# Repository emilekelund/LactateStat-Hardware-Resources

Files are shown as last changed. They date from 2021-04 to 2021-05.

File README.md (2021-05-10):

# LactateStat-Hardware-Resources

This is the hardware resources used in my master thesis: LactateStat: Wearable Electronics and Software for Real-Time Lactate Monitoring in Sweat

The PCB was created using KiCad version 5.1.6 and they were manufactured and assembled by PCBWay.

## Copyright disclaimer

Copyright (c) 2021 Emil Ekelund

Permission is hereby granted, free of charge, to any person obtaining a copy of this software and associated documentation files (the "Software"), to deal in the Software without restriction, including without limitation the rights to use, copy, modify, merge, publish, distribute, sublicense, and/or sell copies of the Software, and to permit persons to whom the Software is furnished to do so, subject to the following conditions:

The above copyright notice and this permission notice shall be included in all copies or substantial portions of the Software.

THE SOFTWARE IS PROVIDED "AS IS", WITHOUT WARRANTY OF ANY KIND, EXPRESS OR IMPLIED, INCLUDING BUT NOT LIMITED TO THE WARRANTIES OF MERCHANTABILITY, FITNESS FOR A PARTICULAR PURPOSE AND NONINFRINGEMENT. IN NO EVENT SHALL THE AUTHORS OR COPYRIGHT HOLDERS BE LIABLE FOR ANY CLAIM, DAMAGES OR OTHER LIABILITY, WHETHER IN AN ACTION OF CONTRACT, TORT OR OTHERWISE, ARISING FROM, OUT OF OR IN CONNECTION WITH THE SOFTWARE OR THE USE OR OTHER DEALINGS IN THE SOFTWARE.

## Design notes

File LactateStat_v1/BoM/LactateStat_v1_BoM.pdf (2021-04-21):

Item | Designator | Description / Value | Package | Manufacturer | Manufacturer part # | Quantity
1 | R205,R204 | 120 | R_0201_0603Metric | | | 2
2 | D201 | LED RED | D_0402_1005Metric | | | 1
3 | D202 | LED GREEN | D_0402_1005Metric | | | 1
4 | R202,R201 | 5.1k | R_0201_0603Metric | | | 2
5 | C101,C102,C112,C113 | 12pF NP0 2% | C_0402_1005Metric | | | 4
6 | C103,C104,C107,C301 | 100nF, X7R, 10% | C_0402_1005Metric | | | 4
7 | C105 | 4.7uF, X5R, 10% | C_0603_1608Metric | | | 1
8 | C106 | 1.0uF X7R 10% | C_0603_1608Metric | | | 1
9 | C108 | 100pF, NP0, 5% | C_0402_1005Metric | | | 1
10 | C110 | 0.8pF, NP0, 5% | C_0402_1005Metric | | | 1
11 | L101 | 3.9nH 5% | L_0402_1005Metric | | | 1
12 | U101 | NRF52832-QFAB-R | 48-VFQFN | | | 1
13 | X101 | 32.768kHz 9pF 20ppm | Crystal_SMD_3215-2Pin_3.2x1.5mm | | | 1
14 | X102 | 32MHz 8pF 10ppm | Crystal_SMD_2016-4Pin_2.0x1.6mm | | | 1
15 | C201,C202 | 4.7uF X7R | C_0402_1005Metric | | | 2
16 | C203,C204 | 1uF | C_0402_1005Metric | | | 2
17 | C302 | 2.2uF | C_0201_0603Metric | | | 1
18 | C303 | 82nF 10% | C_0402_1005Metric | | | 1
20 | J201 | USB C RECEPTACLE | GCT_USB4105_REVA | GCT | USB4110-GF-A | 1
23 | R203 | 10k | R_0402_1005Metric | | | 1
24 | R301 | 10k | R_0201_0603Metric | | | 1
25 | R302 | 1.5M 1% | R_0402_1005Metric | | | 1
26 | SW201 | SW_SPDT | CL-SB-12B | Nidec Copal Electronics | CL-SB-12B-01T | 1
27 | U201 | MCP73831 | SOT-23-5 | | | 1
28 | U202 | TLV73333PDBV | SOT-23-5 | | | 1
29 | U301 | LMP91000SD_NOPB | WSON-14-1EP_4.0x4.0mm_P0.5mm_EP2.6x2.6mm | | | 1

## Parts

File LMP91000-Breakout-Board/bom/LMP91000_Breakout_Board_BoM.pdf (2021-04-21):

Id Designator Package | Quantity Designation | Supplier and ref | Unit Price ($)
1 LMP91000 WSON-14-1EP_4.0x4.0mm_P0.5mm_EP2.6x2.6mm | 1 LMP91000SD_NOPB Texas Instruments LMP91000SD/NOPB | 5
2 R2,R1 | R_0603_1608Metric_Pad1.05x0.95mm_HandSolder | 2 10K | Stackpole Electronics Inc RNCP0603FTD10K0 | 0,1
3 C2 | C_0603_1608Metric_Pad1.05x0.95mm_HandSolder | 1 1u | Samsung Electro-Mechanics CL10B104KB8NNNL | 0,1
4 C1 | C_0603_1608Metric_Pad1.05x0.95mm_HandSolder | 1 0.1u | Samsung Electro-Mechanics CL10B105KP8NNNC | 0,1

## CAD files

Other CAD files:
Case/LactateStat_3D_Printed_Case.dwg

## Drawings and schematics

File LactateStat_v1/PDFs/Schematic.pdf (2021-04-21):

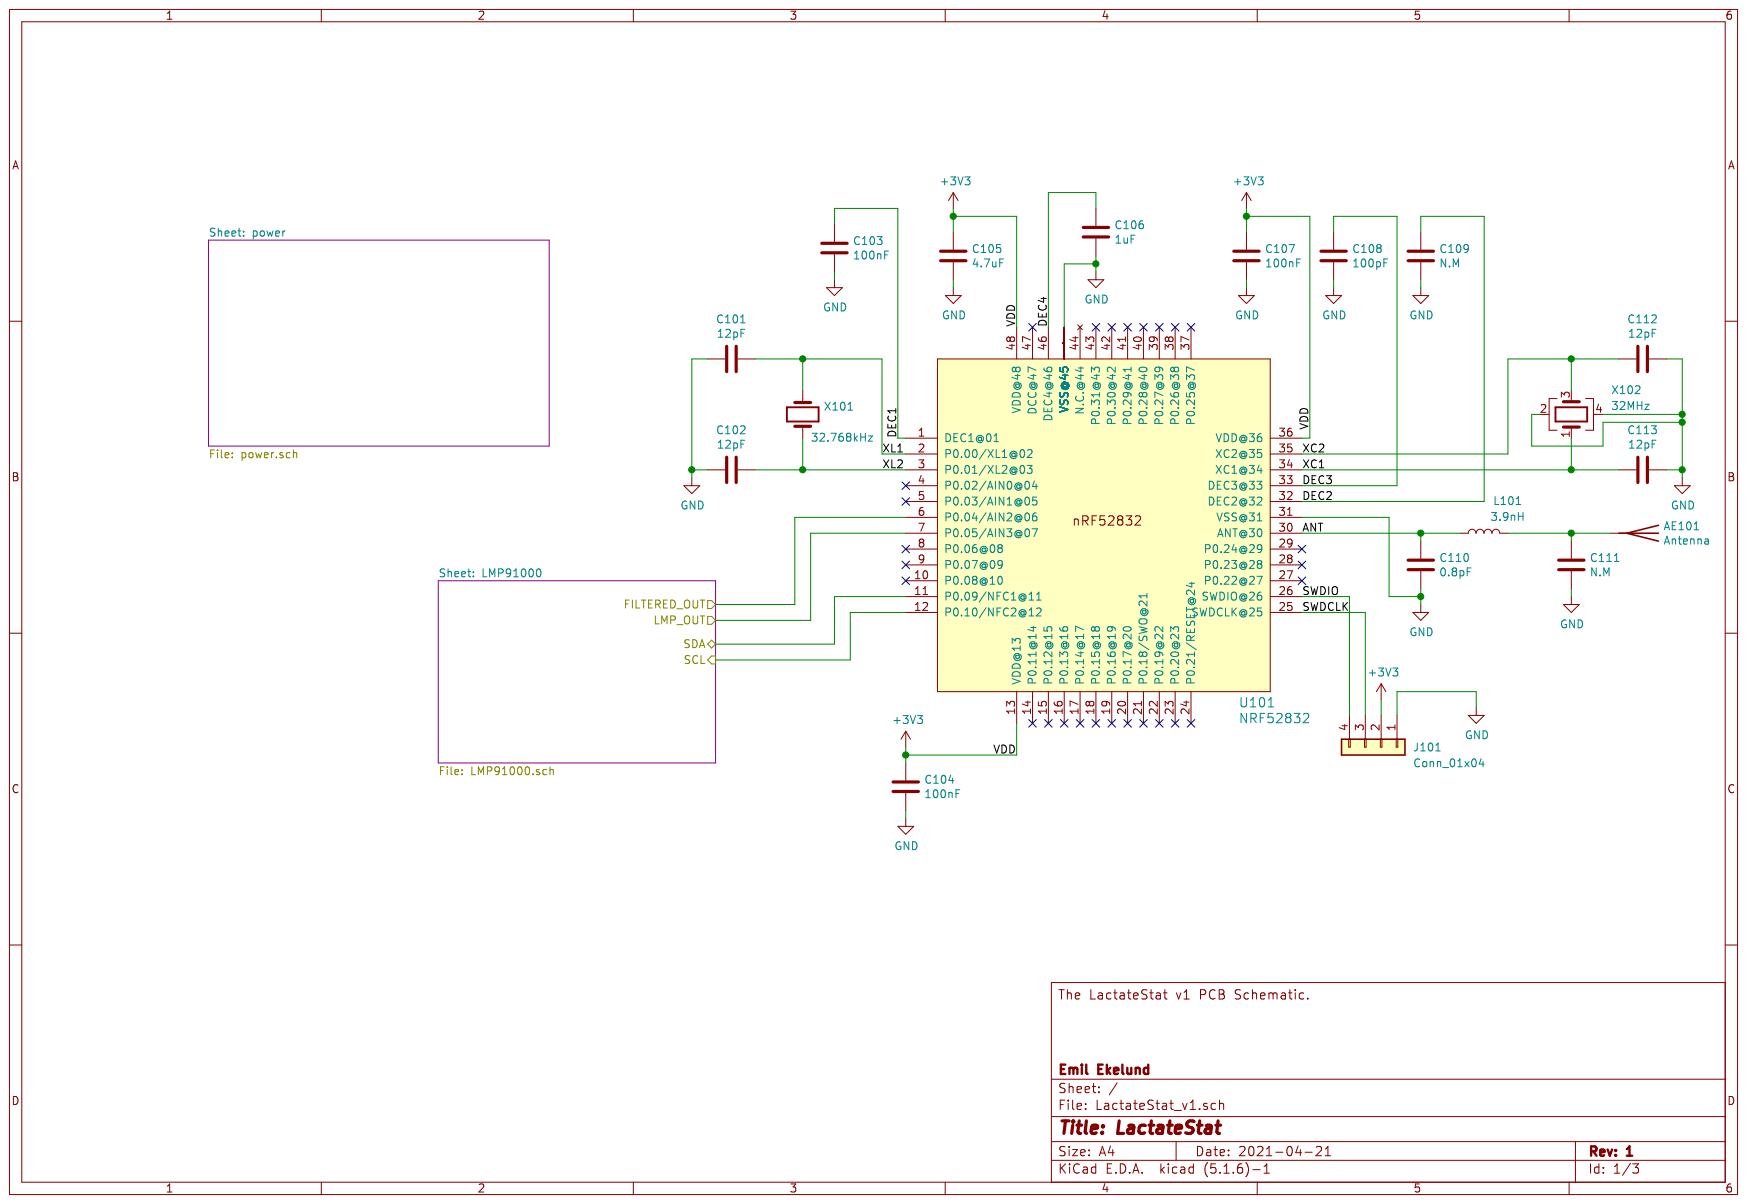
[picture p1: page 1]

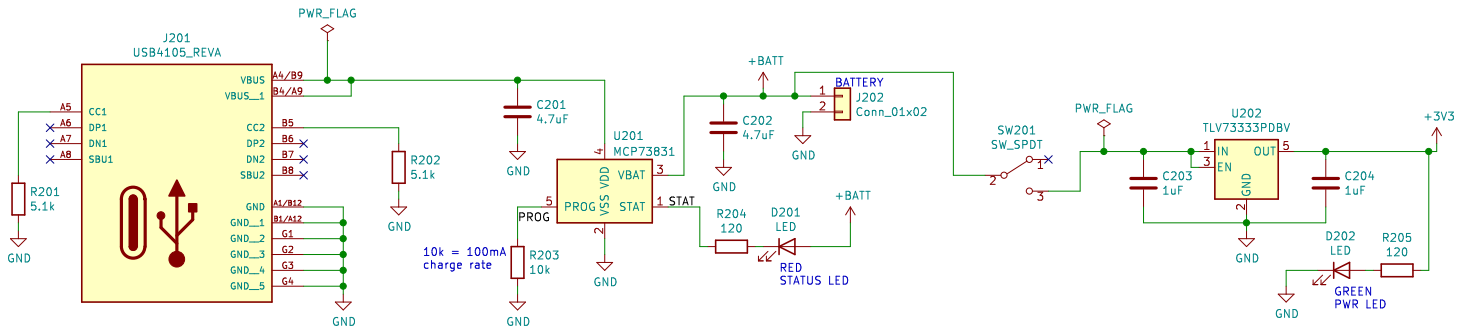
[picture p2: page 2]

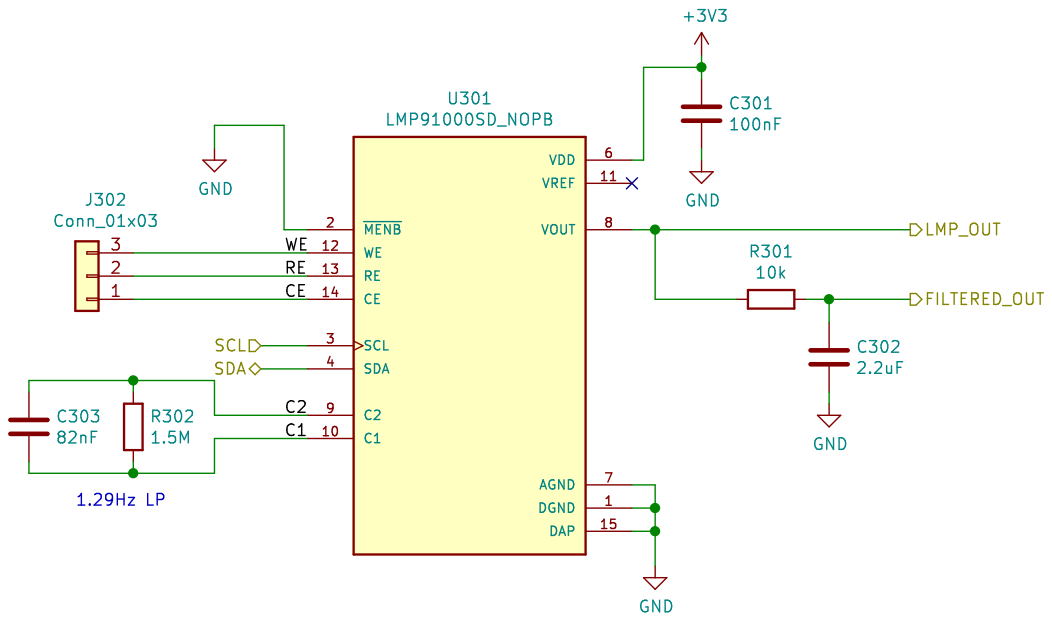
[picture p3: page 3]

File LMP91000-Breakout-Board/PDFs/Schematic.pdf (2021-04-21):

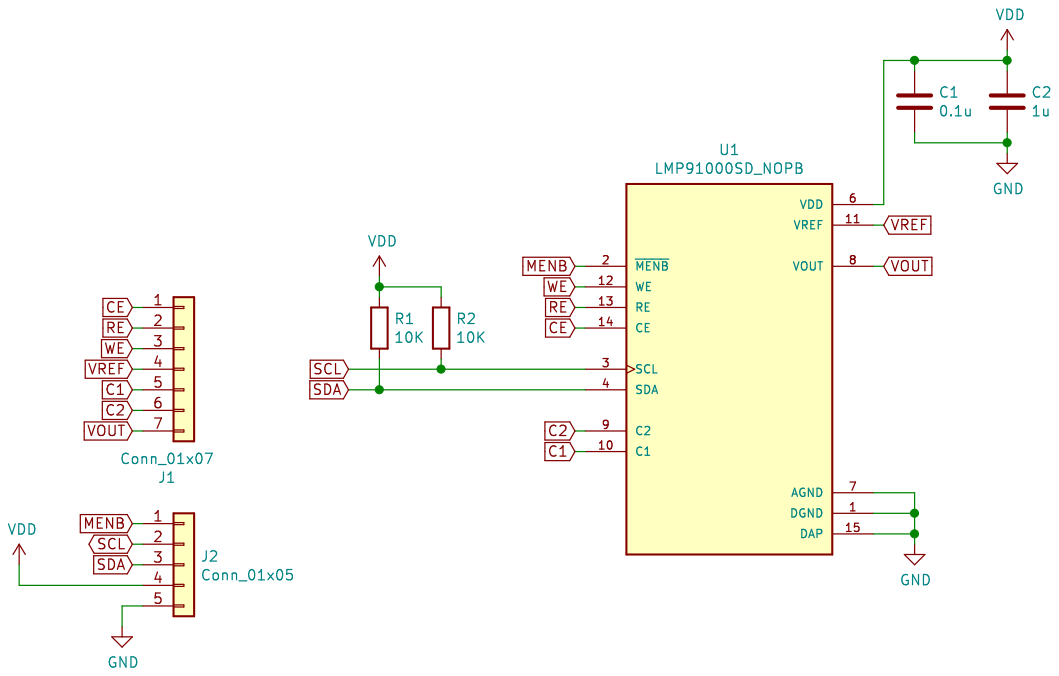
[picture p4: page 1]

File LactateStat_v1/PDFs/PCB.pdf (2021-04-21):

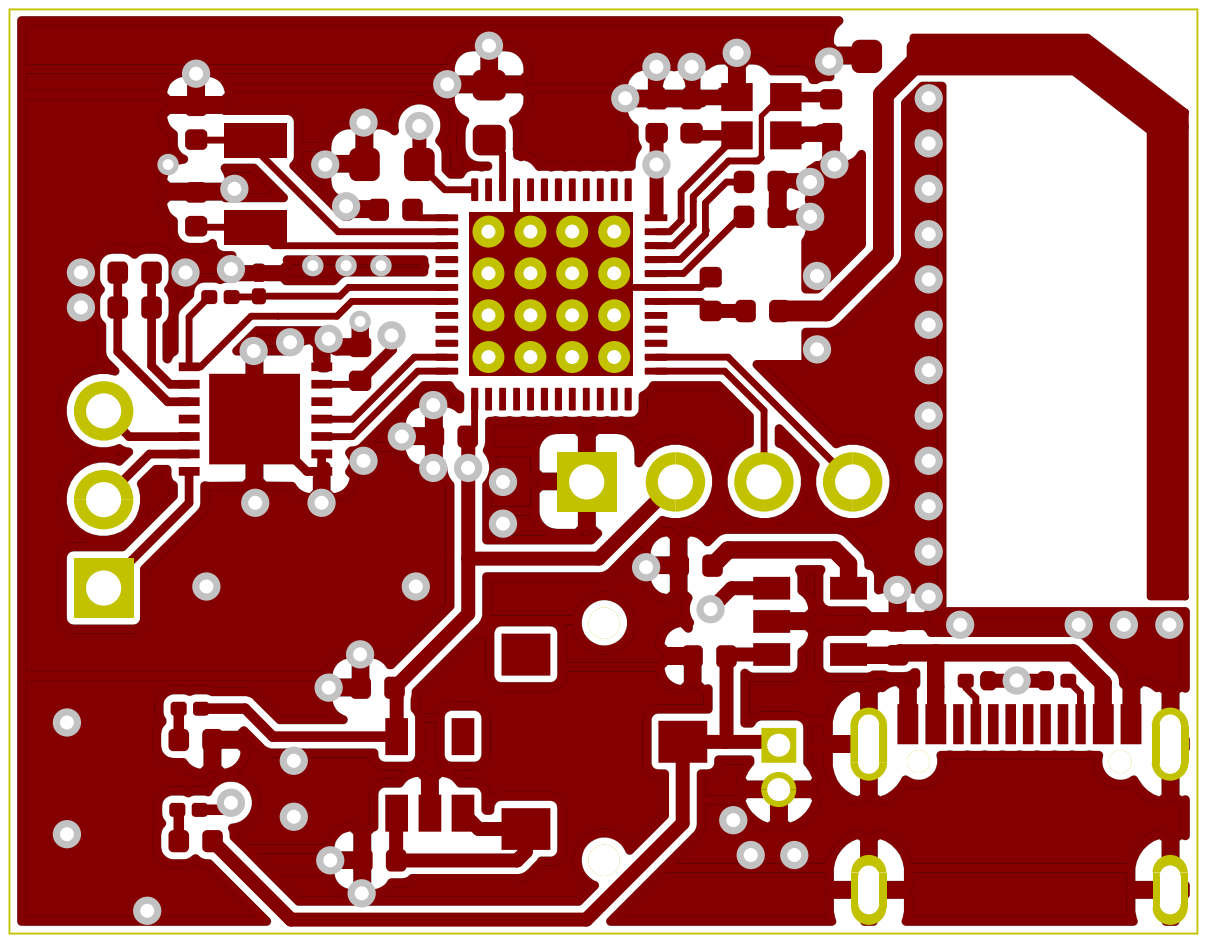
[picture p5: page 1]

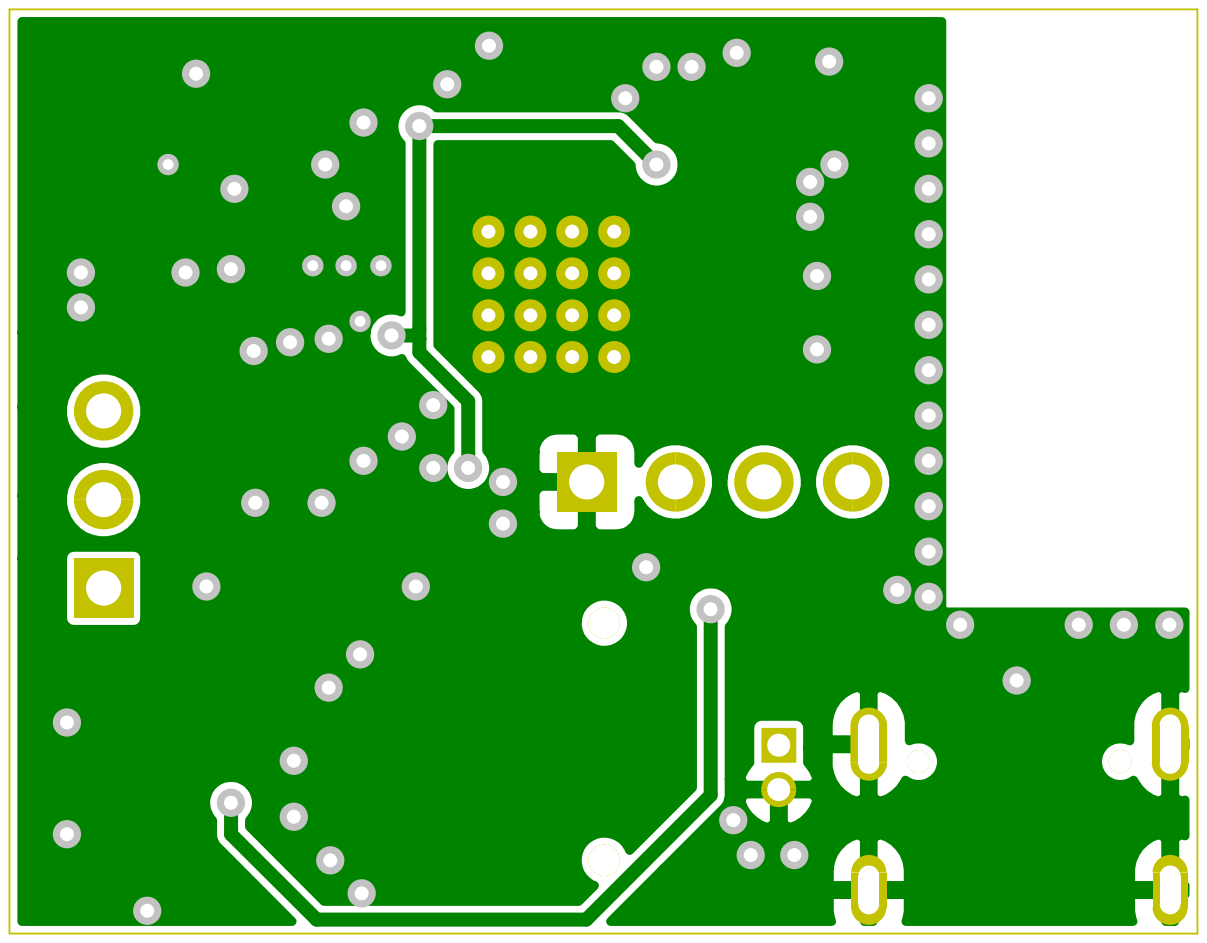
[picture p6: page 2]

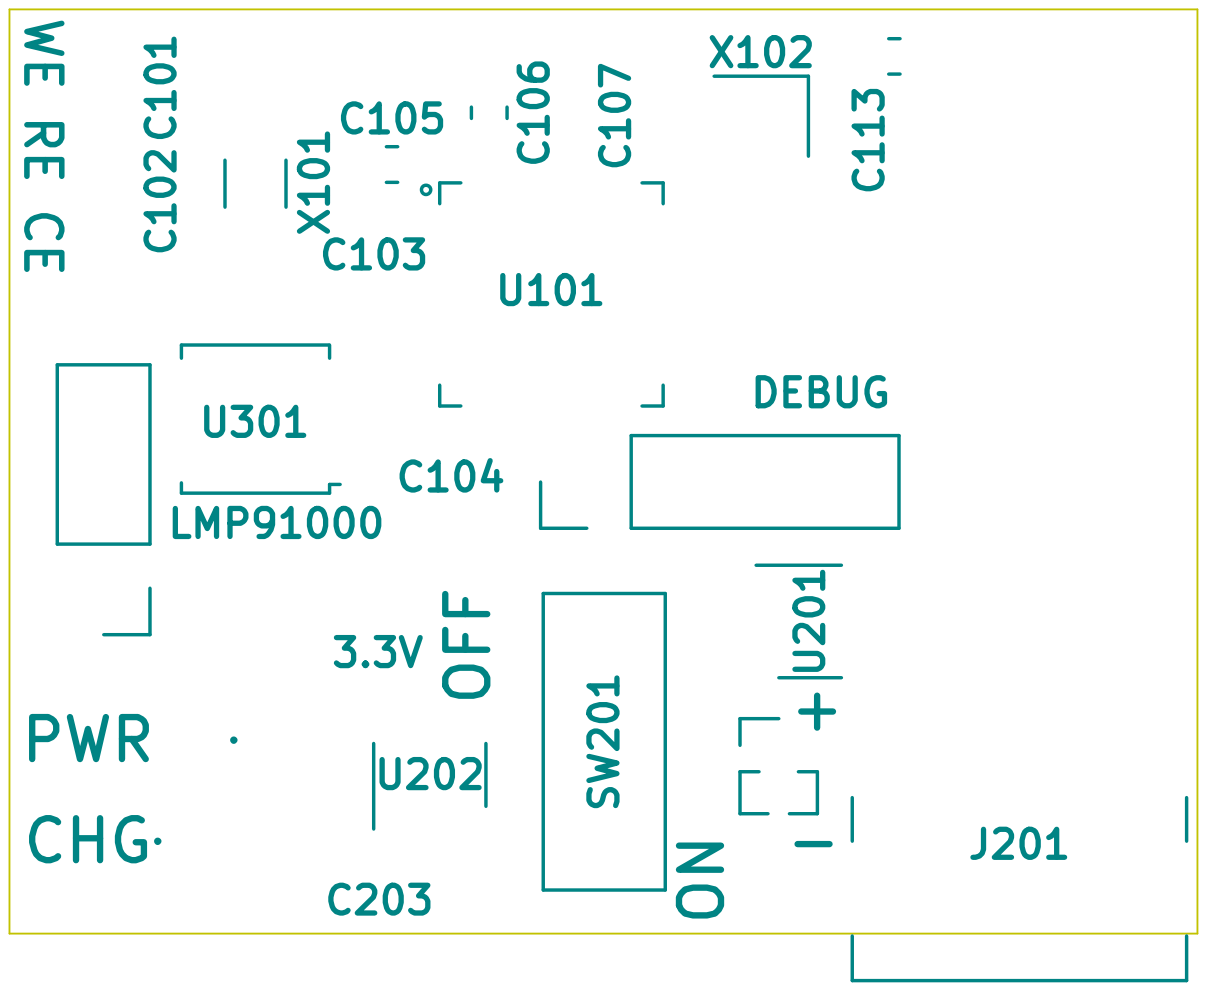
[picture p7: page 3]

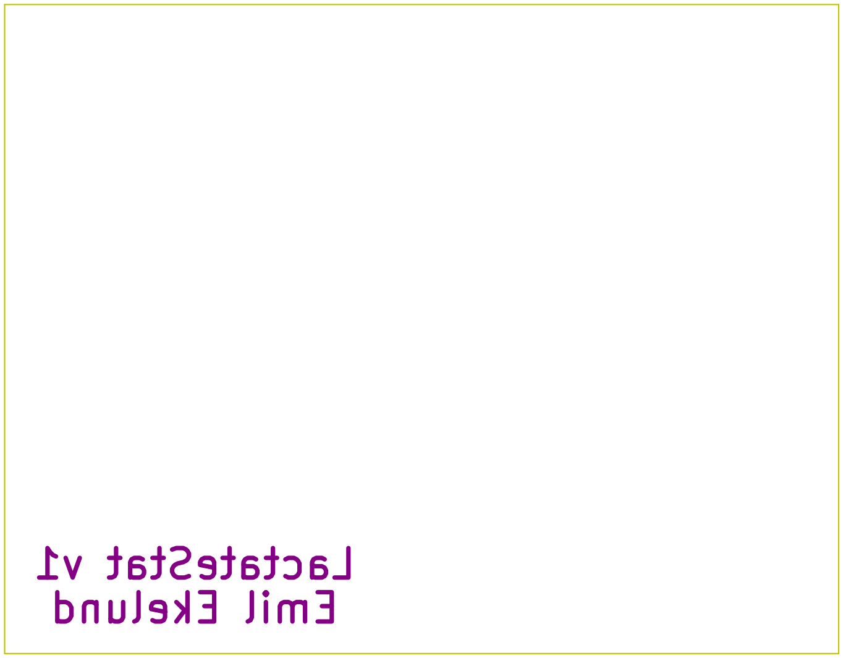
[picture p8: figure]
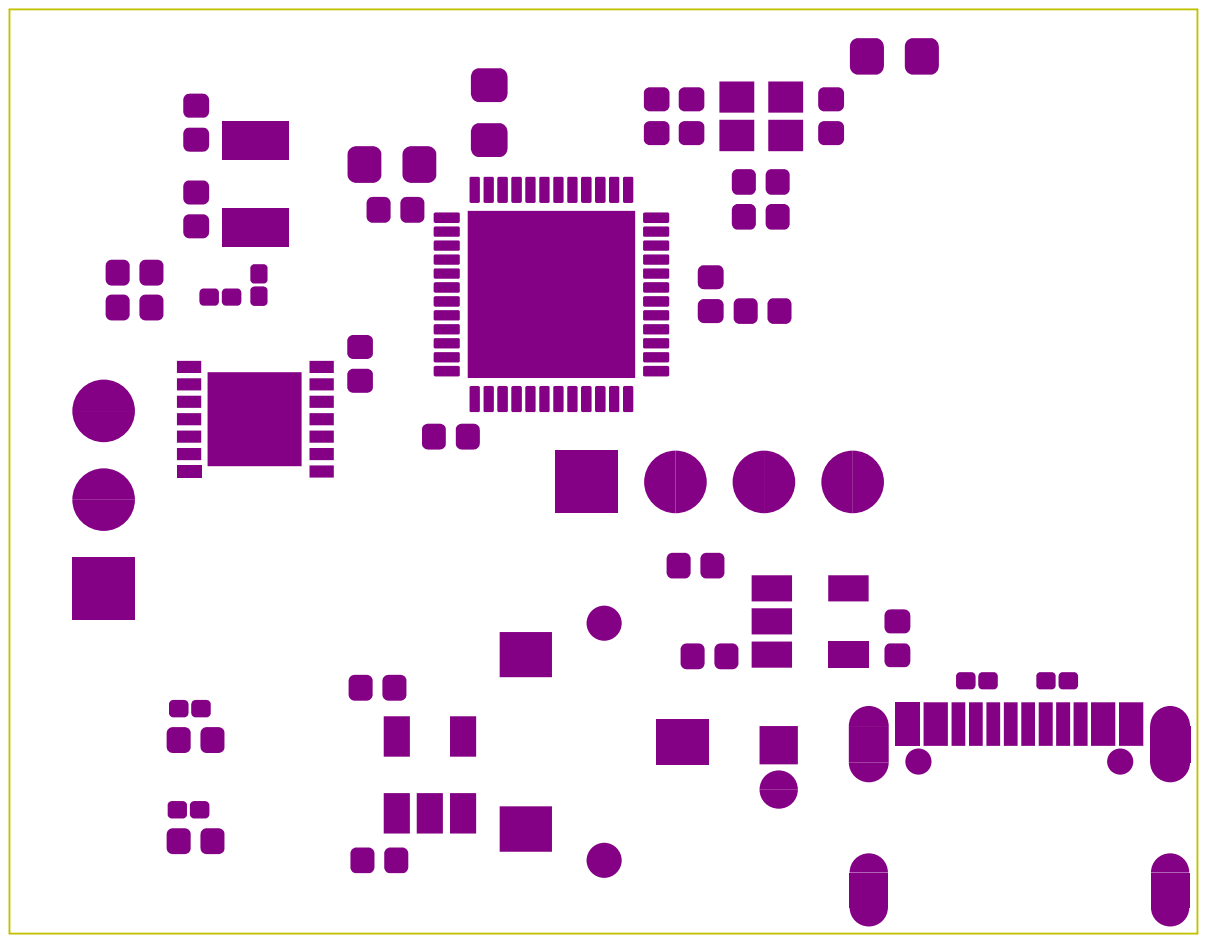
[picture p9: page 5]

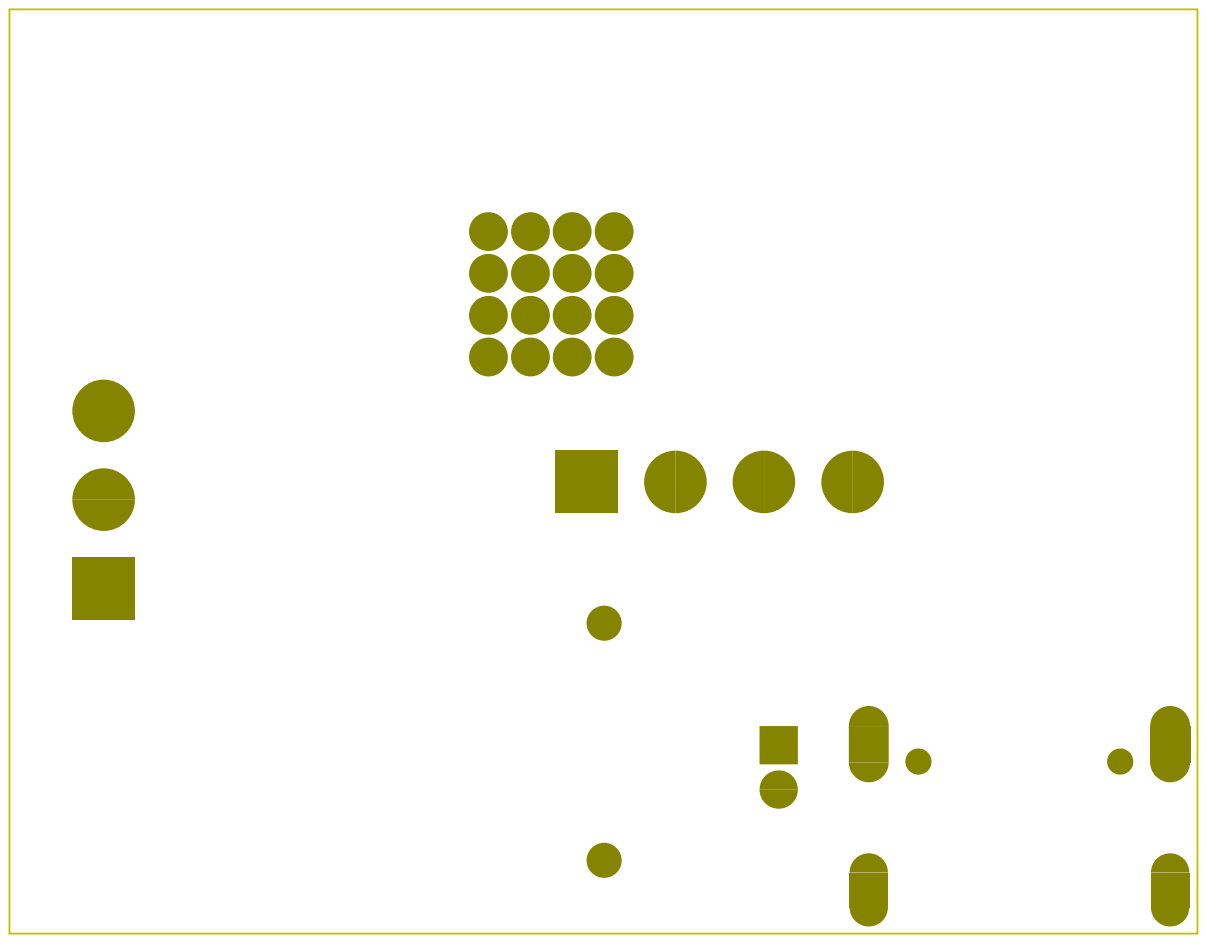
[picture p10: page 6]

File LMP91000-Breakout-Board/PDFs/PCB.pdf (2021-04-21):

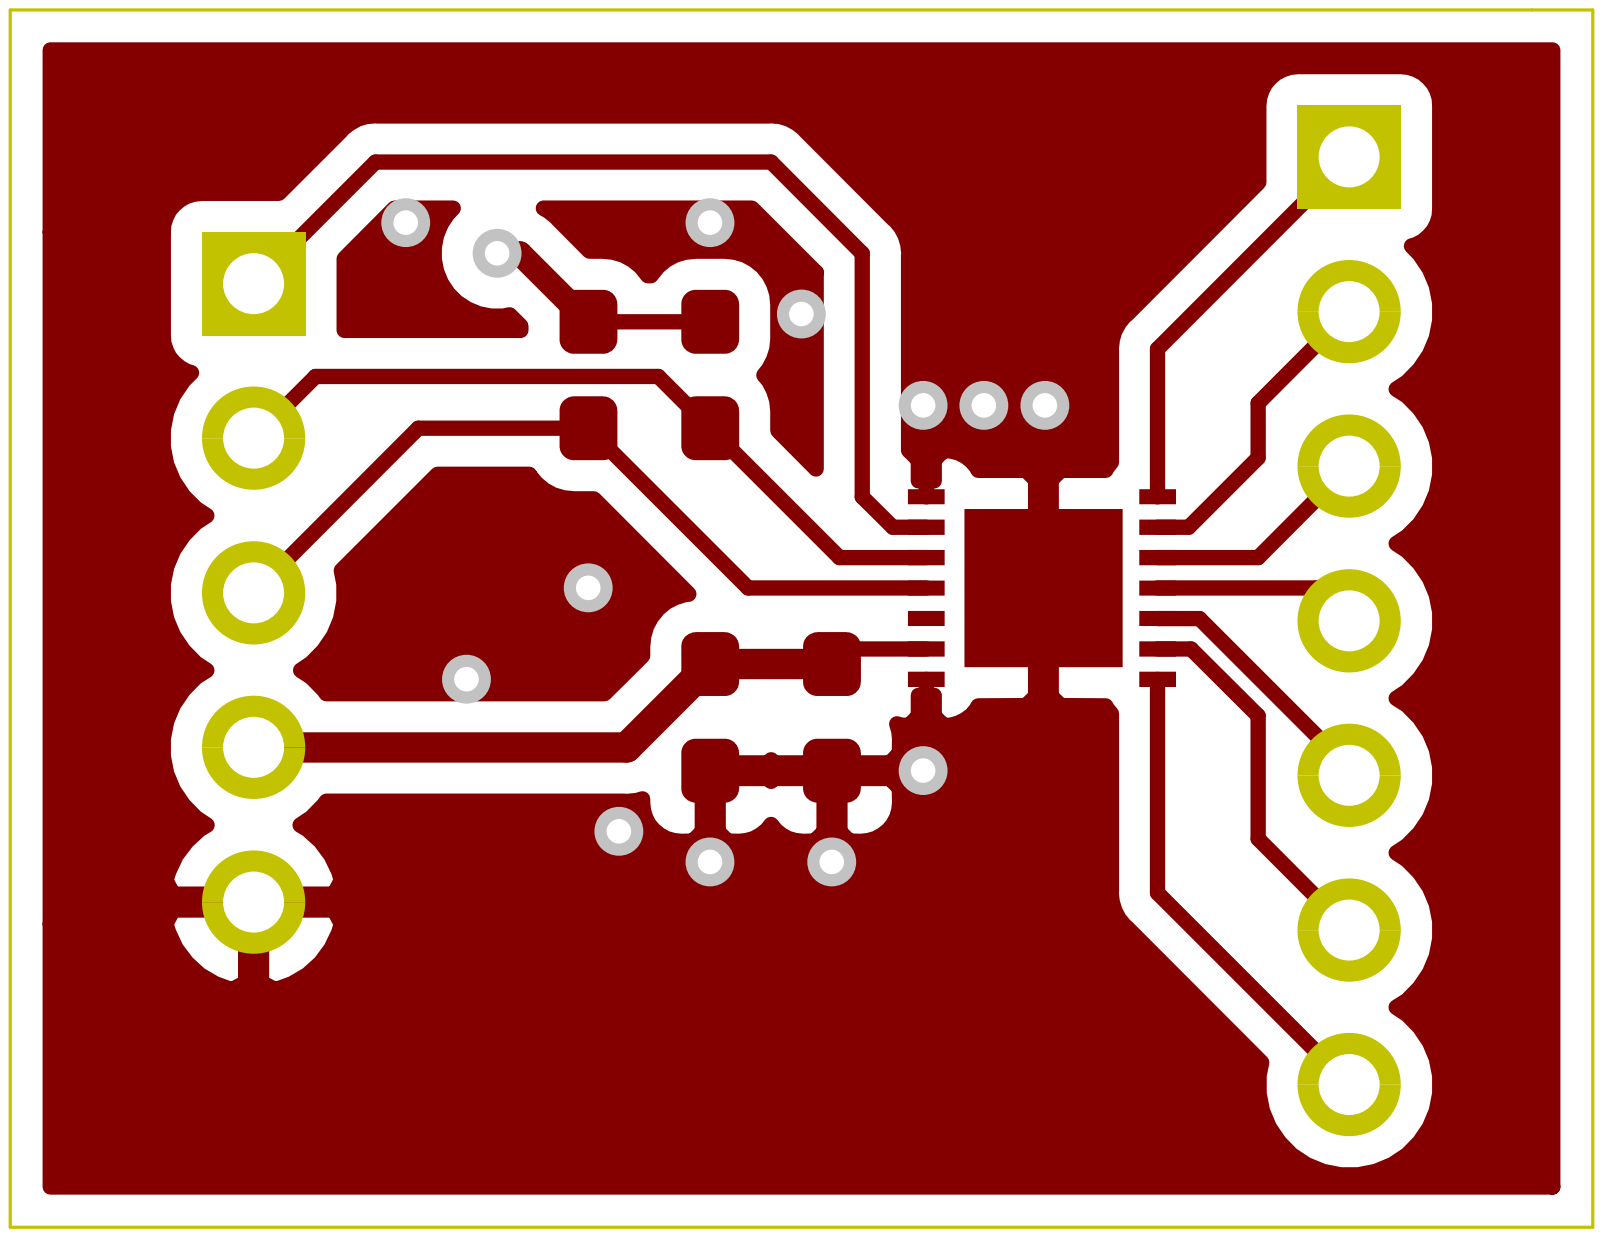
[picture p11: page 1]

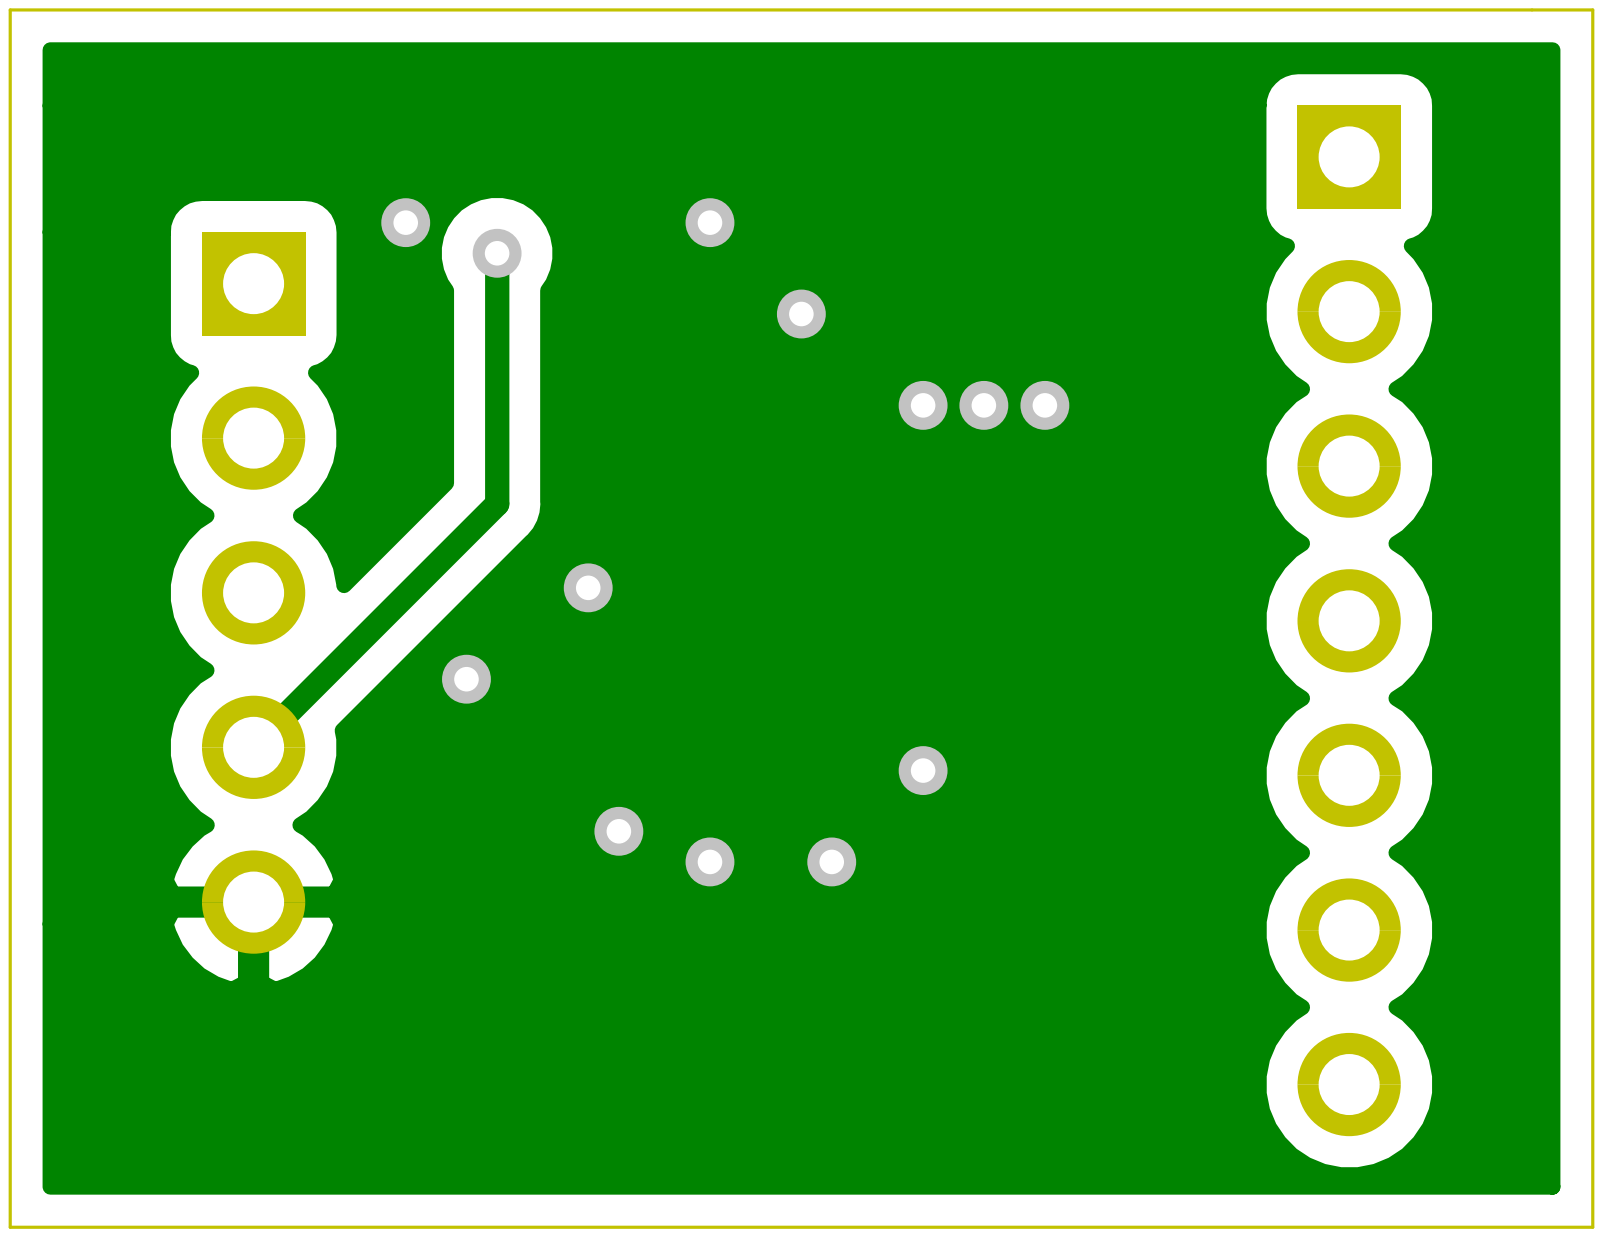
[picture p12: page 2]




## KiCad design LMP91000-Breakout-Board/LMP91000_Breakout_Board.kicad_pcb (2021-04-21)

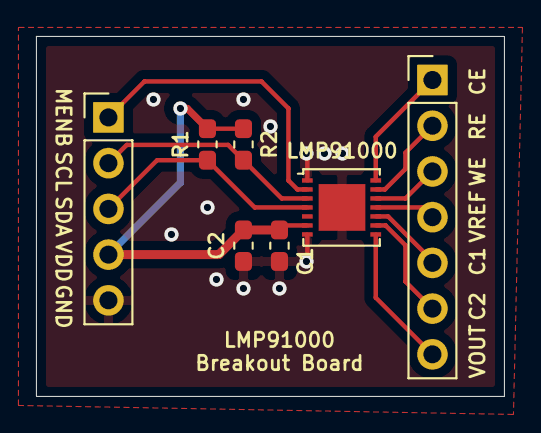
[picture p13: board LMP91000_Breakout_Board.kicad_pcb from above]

Board: 2 copper layers, 26.0 x 20.0 mm, 7 parts (0 on the bottom side), 12 nets.

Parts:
C1: 0.1u; C_0603_1608Metric_Pad1.05x0.95mm_HandSolder
C2: 1u; C_0603_1608Metric_Pad1.05x0.95mm_HandSolder
J1: Conn_01x07; PinHeader_1x07_P2.54mm_Vertical
J2: Conn_01x05; PinHeader_1x05_P2.54mm_Vertical
LMP91000: LMP91000SD_NOPB; WSON-14-1EP_4.0x4.0mm_P0.5mm_EP2.6x2.6mm
R1, R2: 10K; R_0603_1608Metric_Pad1.05x0.95mm_HandSolder

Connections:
C1: J1.5, LMP91000.10
C2: J1.6, LMP91000.9
CE: J1.1, LMP91000.14
GND: C1.2, C2.2, J2.5, LMP91000.1, LMP91000.7, LMP91000.15
MENB: J2.1, LMP91000.2
RE: J1.2, LMP91000.13
SCL: J2.2, LMP91000.3, R2.2
SDA: J2.3, LMP91000.4, R1.2
VDD: C1.1, C2.1, J2.4, LMP91000.6, R1.1, R2.1
VOUT: J1.7, LMP91000.8
VREF: J1.4, LMP91000.11
WE: J1.3, LMP91000.12

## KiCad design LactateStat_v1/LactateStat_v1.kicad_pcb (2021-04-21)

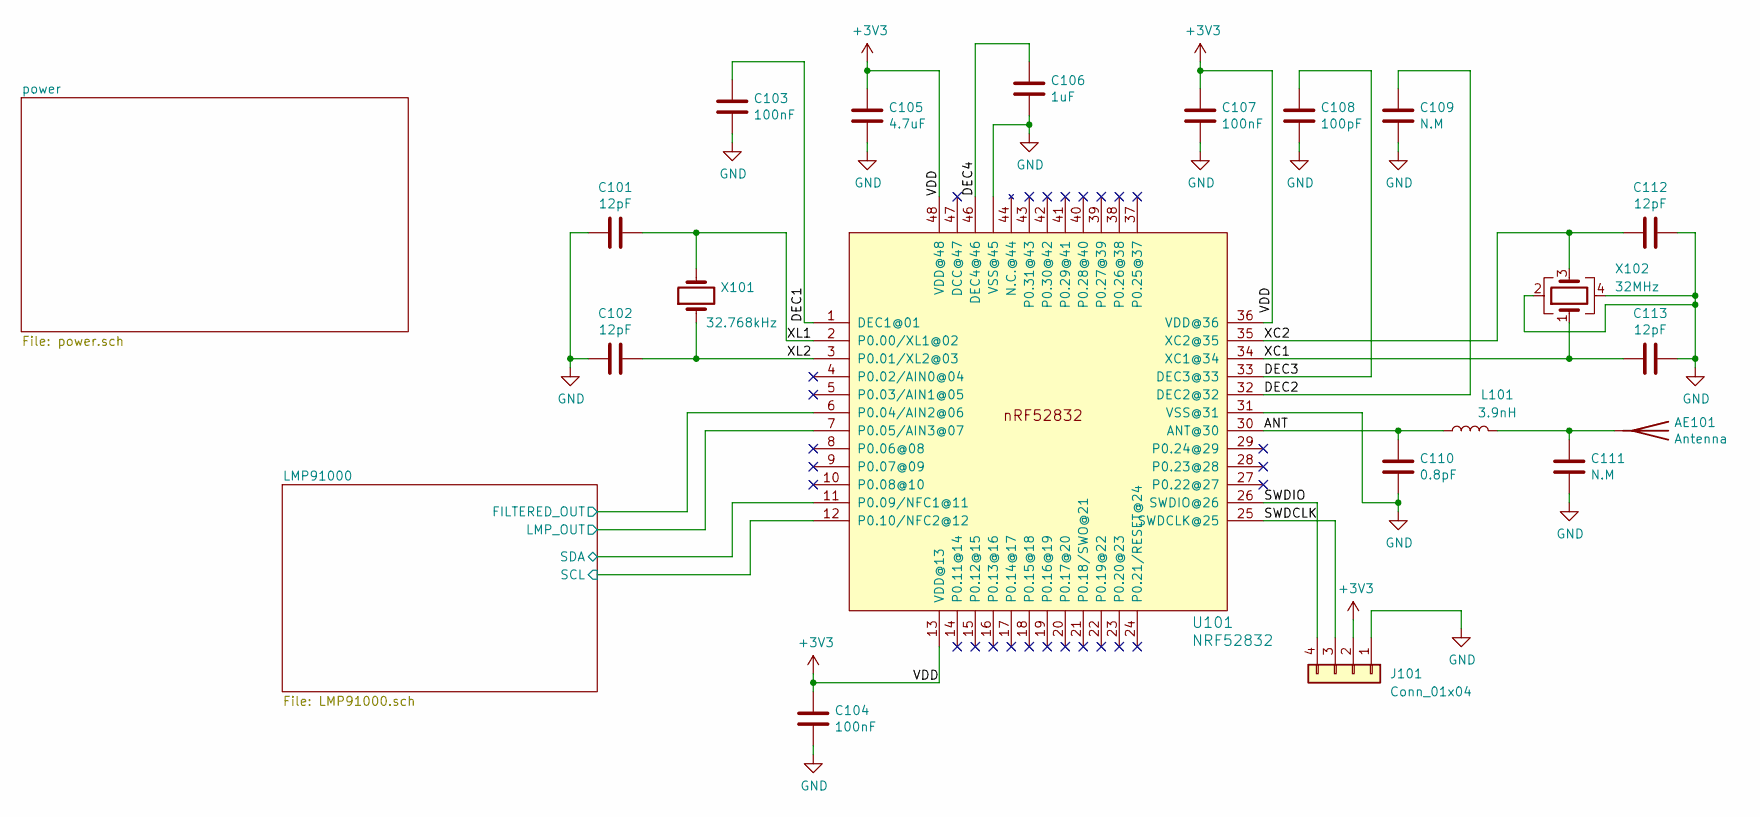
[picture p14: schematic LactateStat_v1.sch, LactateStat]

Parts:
AE101: Antenna
C101, C102, C112, C113: 12pF; C_0402_1005Metric
C103, C104, C107: 100nF; C_0402_1005Metric
C105: 4.7uF; C_0603_1608Metric
C106: 1uF; C_0603_1608Metric
C108: 100pF; C_0402_1005Metric
C109: N.M; C_0402_1005Metric
C110: 0.8pF; C_0402_1005Metric
C111: N.M; C_0603_1608Metric
J101: Conn_01x04; PinHeader_1x04_P2.54mm_Vertical
L101: 3.9nH; L_0402_1005Metric
U101: NRF52832; nRF52832_with_via_pads
X101: 32.768kHz; Crystal_SMD_3215-2Pin_3.2x1.5mm
X102: 32MHz; Crystal_SMD_2016-4Pin_2.0x1.6mm

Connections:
+3V3: C104.1, C105.1, C107.1, J101.2, U101.13 (VDD@13), U101.36 (VDD@36), U101.48 (VDD@48); also elsewhere on the board
/ANT: C110.1, L101.1, U101.30 (ANT@30)
/DEC1: C103.1, U101.1 (DEC1@01)
/DEC2: C109.1, U101.32 (DEC2@32)
/DEC3: C108.1, U101.33 (DEC3@33)
/DEC4: C106.1, U101.46 (DEC4@46)
/LMP91000/FILTERED_OUT: U101.6 (P0.04/AIN2@06); also elsewhere on the board
/LMP91000/LMP_OUT: U101.7 (P0.05/AIN3@07); also elsewhere on the board
/LMP91000/SCL: U101.12 (P0.10/NFC2@12); also elsewhere on the board
/LMP91000/SDA: U101.11 (P0.09/NFC1@11); also elsewhere on the board
/SWDCLK: J101.3, U101.25 (SWDCLK@25)
/SWDIO: J101.4, U101.26 (SWDIO@26)
/XC1: C113.2, U101.34 (XC1@34), X102.1
/XC2: C112.2, U101.35 (XC2@35), X102.3
/XL1: C101.1, U101.2 (P0.00/XL1@02), X101.2
/XL2: C102.1, U101.3 (P0.01/XL2@03), X101.1
GND: C101.2, C102.2, C103.2, C104.2, C105.2, C106.2, C107.2, C108.2, C109.2, C110.2, C111.2, C112.1, C113.1, J101.1, U101.31 (VSS@31), U101.45 (VSS@45), U101.PAD (VSS@45), U101.PAD@VIA01 (VSS@45), U101.PAD@VIA02 (VSS@45), U101.PAD@VIA03 (VSS@45), U101.PAD@VIA04 (VSS@45), U101.PAD@VIA05 (VSS@45), U101.PAD@VIA06 (VSS@45), U101.PAD@VIA07 (VSS@45), U101.PAD@VIA08 (VSS@45), U101.PAD@VIA09 (VSS@45), U101.PAD@VIA10 (VSS@45), U101.PAD@VIA11 (VSS@45), U101.PAD@VIA12 (VSS@45), U101.PAD@VIA13 (VSS@45), U101.PAD@VIA14 (VSS@45), U101.PAD@VIA15 (VSS@45), U101.PAD@VIA16 (VSS@45), X102.2, X102.4; also elsewhere on the board
unnamed: AE101.1, C111.1, L101.2

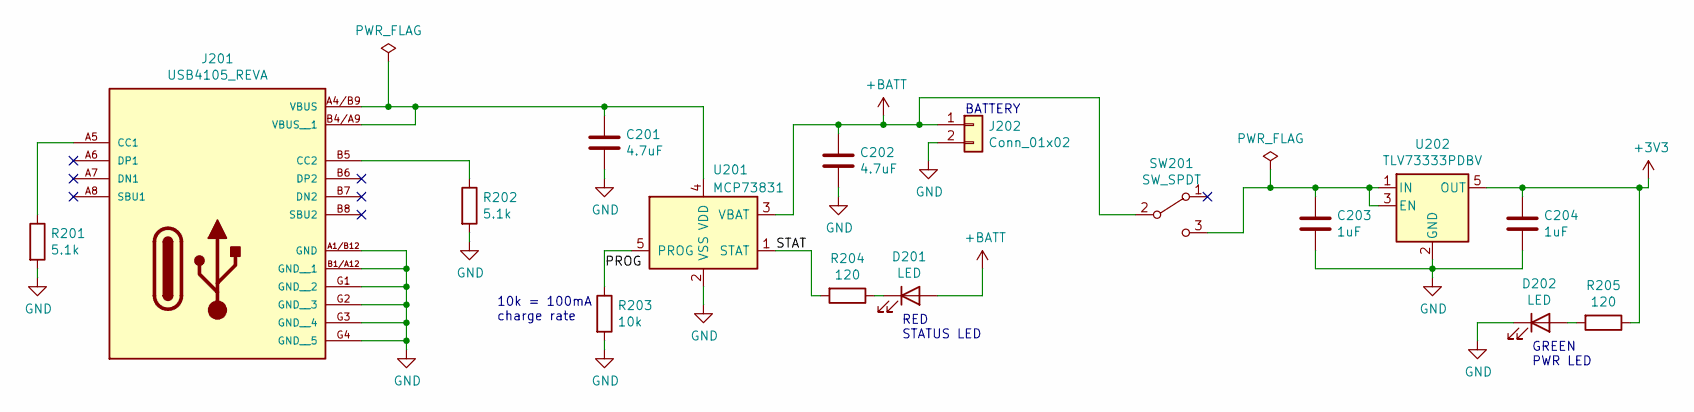
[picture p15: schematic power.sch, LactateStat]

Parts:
C201, C202: 4.7uF; C_0402_1005Metric
C203, C204: 1uF; C_0402_1005Metric
D201, D202: LED; D_0402_1005Metric
J201: USB4105_REVA; GCT_USB4105_REVA
J202: Conn_01x02; PinHeader_1x02_P1.27mm_Vertical
R201, R202: 5.1k; R_0201_0603Metric
R203: 10k; R_0402_1005Metric
R204, R205: 120; R_0201_0603Metric
SW201: SW_SPDT; CL-SB-12B
U201: MCP73831; SOT-23-5
U202: TLV73333PDBV; SOT-23-5

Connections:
+3V3: C204.1, R205.1, U202.5 (OUT); also elsewhere on the board
+BATT: C202.1, D201.2 (A), J202.1, SW201.2 (B), U201.3 (VBAT)
/power/PROG: R203.1, U201.5 (PROG)
/power/STAT: R204.2, U201.1 (STAT)
GND: C201.2, C202.2, C203.2, C204.2, D202.1 (K), J201.A1/B12 (GND), J201.B1/A12 (GND__1), J201.G1 (GND__2), J201.G2 (GND__3), J201.G3 (GND__4), J201.G4 (GND__5), J202.2, R201.2, R202.2, R203.2, U201.2 (VSS), U202.2 (GND); also elsewhere on the board
unnamed: C201.1, J201.A4/B9 (VBUS), J201.B4/A9 (VBUS__1), U201.4 (VDD)
unnamed: C203.1, SW201.3 (C), U202.1 (IN), U202.3 (EN)
unnamed: D201.1 (K), R204.1
unnamed: D202.2 (A), R205.2
unnamed: J201.A5 (CC1), R201.1
unnamed: J201.B5 (CC2), R202.1

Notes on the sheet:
10k = 100mA charge rate
RED STATUS LED
GREEN PWR LED
BATTERY

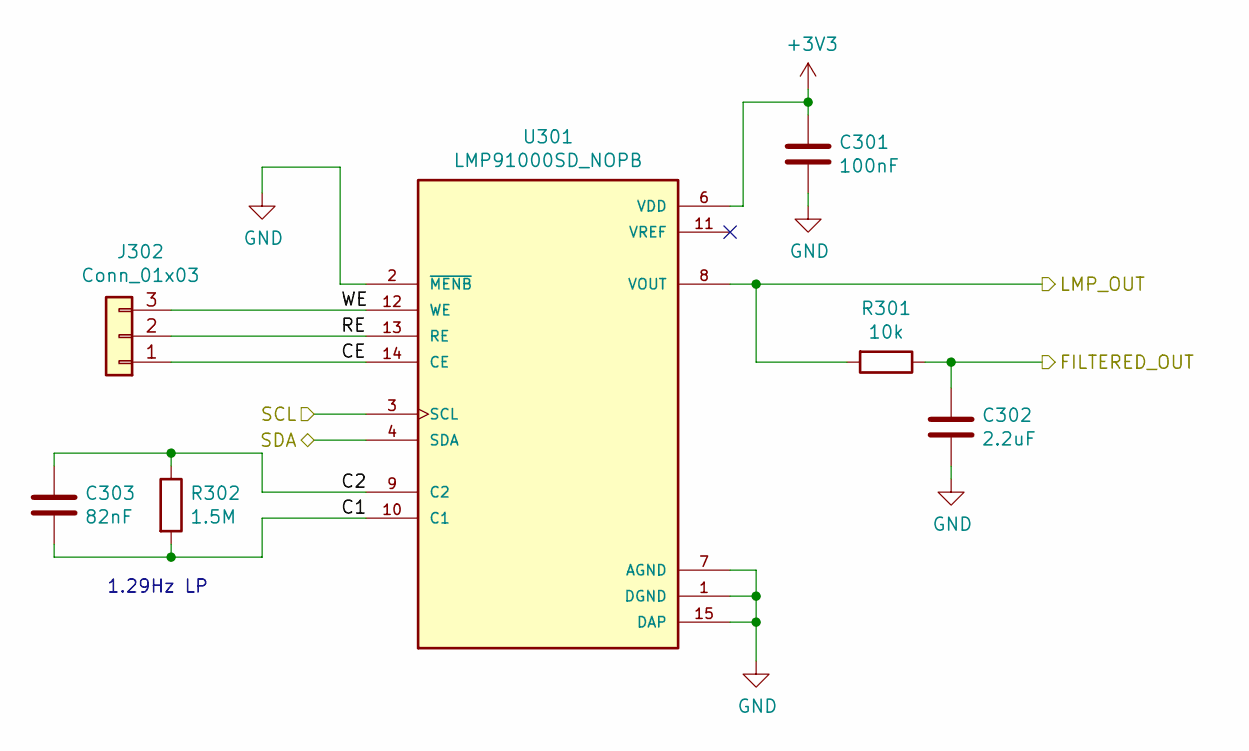
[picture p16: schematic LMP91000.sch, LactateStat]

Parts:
C301: 100nF; C_0402_1005Metric
C302: 2.2uF; C_0201_0603Metric
C303: 82nF; C_0402_1005Metric
J302: Conn_01x03; PinHeader_1x03_P2.54mm_Vertical
R301: 10k; R_0201_0603Metric
R302: 1.5M; R_0402_1005Metric
U301: LMP91000SD_NOPB; WSON-14-1EP_4.0x4.0mm_P0.5mm_EP2.6x2.6mm; PARTREV I

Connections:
+3V3: C301.1, U301.6 (VDD); also elsewhere on the board
/LMP91000/C1: C303.2, R302.2, U301.10 (C1)
/LMP91000/C2: C303.1, R302.1, U301.9 (C2)
/LMP91000/CE: J302.1, U301.14 (CE)
/LMP91000/FILTERED_OUT: C302.1, R301.1; also elsewhere on the board
/LMP91000/LMP_OUT: R301.2, U301.8 (VOUT); also elsewhere on the board
/LMP91000/RE: J302.2, U301.13 (RE)
/LMP91000/SCL: U301.3 (SCL); also elsewhere on the board
/LMP91000/SDA: U301.4 (SDA); also elsewhere on the board
/LMP91000/WE: J302.3, U301.12 (WE)
GND: C301.2, C302.2, U301.1 (DGND), U301.2 (~MENB), U301.7 (AGND), U301.15 (DAP); also elsewhere on the board

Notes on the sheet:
1.29Hz LP

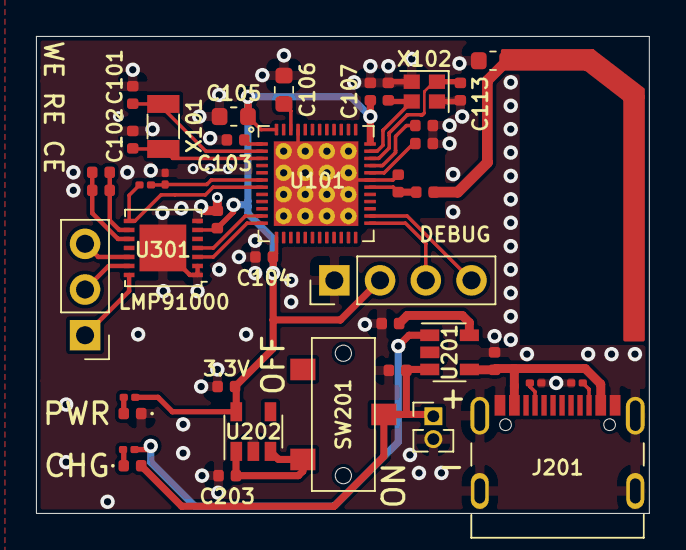
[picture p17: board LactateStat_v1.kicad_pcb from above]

Board: 2 copper layers, 34.1 x 26.5 mm, 41 parts (0 on the bottom side), 32 nets.
